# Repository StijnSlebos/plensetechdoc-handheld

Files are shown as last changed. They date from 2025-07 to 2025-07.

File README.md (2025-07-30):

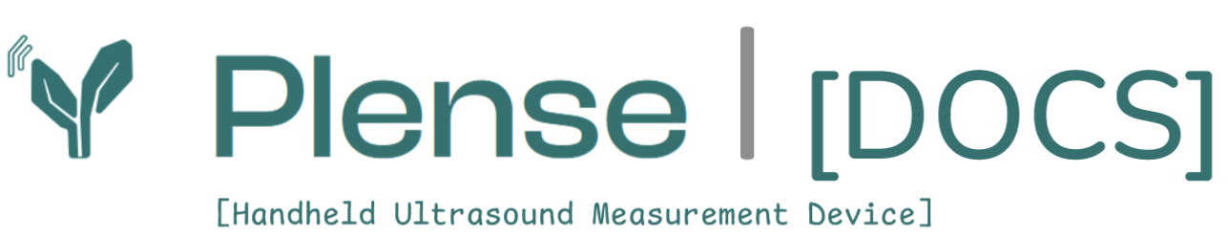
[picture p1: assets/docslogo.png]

# plensetechdoc-handheld
Documentation and code for the ultrasound handheld measuring device built by plense-technologies.

## Overview

A precision-engineered handheld setup for in-situ acoustic measurement of plant stems. The system integrates a force-controlled stepper motor clamp, dual piezoelectric transducers, and a Raspberry Pi GUI. Measurements are triggered by controlled force application and executed via a miniVNA, producing calibrated Touchstone files for further analysis.

## Features

- Arduino-based motor and endstop control
- Force sensor for precise clamping
- Dual piezo transducers for signal transmission/reception
- Signal conditioning hardware
- miniVNA for impedance/transfer measurements
- Raspberry Pi GUI for system control and data capture

---

## Repository Structure

```text
handheld-acoustic-device/
│
├── README.md                   # Top-level documentation overview
│
├── arduino-firmware/           # Firmware for stepper motor and sensor control
│   └── clamp_control.ino
│
├── raspberry-pi-gui/           # Python GUI application for Raspberry Pi
│   ├── README.md               # Installation instructions and user guide
│   ├── requirements.txt        # Python dependencies (pip)
│   ├── calibration/            # Calibration files for nanoVNA
│   │   └── calibration_10-500khz.cal
│   ├── code/                   # GUI and controller source code
│   │   └── *.py
│   └── output/                 # Output folder for measurement results
│       └── metadata.json       # JSON file storing configuration and metadata
│
└── hardware/
    ├── schematics/             # Circuit diagrams and signal conditioning chain
    │   ├── signal_conditioning_chain.pdf
    │   └── arduino_schematics.pdf
    ├── bill_of_materials.md    # Parts list (can also be .xlsx)
    ├── cad/                    # Fusion 360 design files
    │   └── ...
    └── stl/                    # 3D printable models
        └── ...

```
<p float="left">
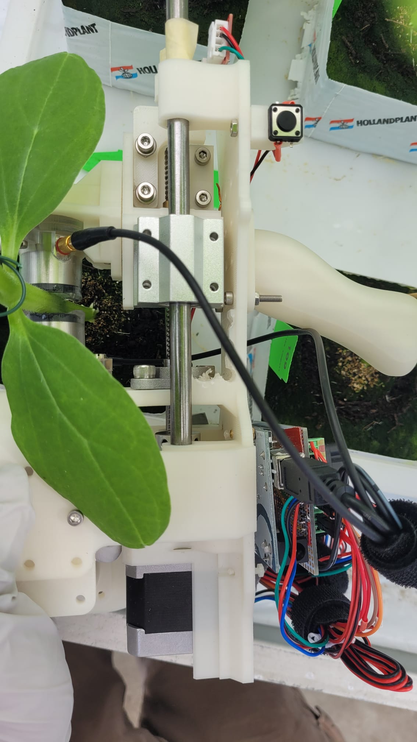
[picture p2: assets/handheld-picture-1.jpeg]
  
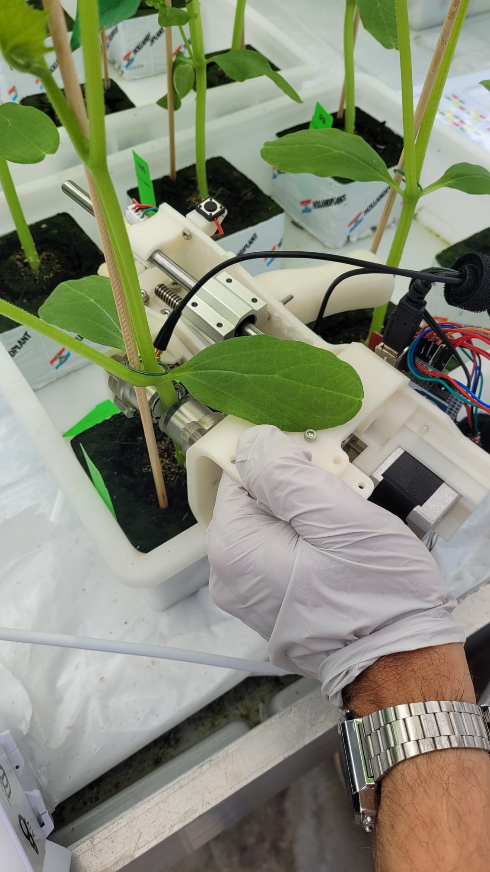
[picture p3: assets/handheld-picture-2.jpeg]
  
</p>

---

## 1. **Introduction**
Welcome to the startup guide for using our handheld plant acoustic sensing system. This document provides an overview of system components, setup procedures, operating routines, and background theory. This device and its applicability and methodology are developed by plense technologies in 2023-2025. The goal of this device is to measure accoustics through the stem of a plant and part of a sensor development project. 

The produced data from this setup can be analyzed using the [developed data-tools in this](https://github.com/StijnSlebos/plensetechdoc-dataanalysis) repository.
Our other related projects for [passive audio capture](https://github.com/StijnSlebos/plensetechdoc-passiveaudiocapture) and for the [plensor multisensor system](https://github.com/StijnSlebos/plensetechdoc-sensoredgecode) can be found in their respective repositories.

For any questions related to this project please reach into the discussiong tab (and perhaps your question is already answered there!).

Below you will walk through the system description, the setup-guide, a walkthrough of usage, a startup explanation of the data-analysis with touchstone files and lastly a troubleshooting guide. The subsections below will cover theoretical background and goals. 

### 1.1 **How It Works: Ultrasound sensing**
The system analyzes the frequency-dependent transmission characteristics of acoustic signals through the plant stem, reflecting physiological and structural traits. The stem is clamped and probed using piezo transducers, while signal analysis is conducted via the nanoVNA. Coordination is handled by the Raspberry Pi and Arduino.

### 1.2 **Theoretical Background: why would you sense ultrasound in a plant**
#### Acoustic Impedance and Frequency Transmission
- Frequency-dependent impedance and transfer response represent internal mechanical structure
- Influenced by stem stiffness, geometry, water content, and health status

#### Plant Sensing Rationale
- Transfer functions provide insights into physiological condition
- Non-destructive and consistent over time

## 2. **System Components**
_images speak louder than words_
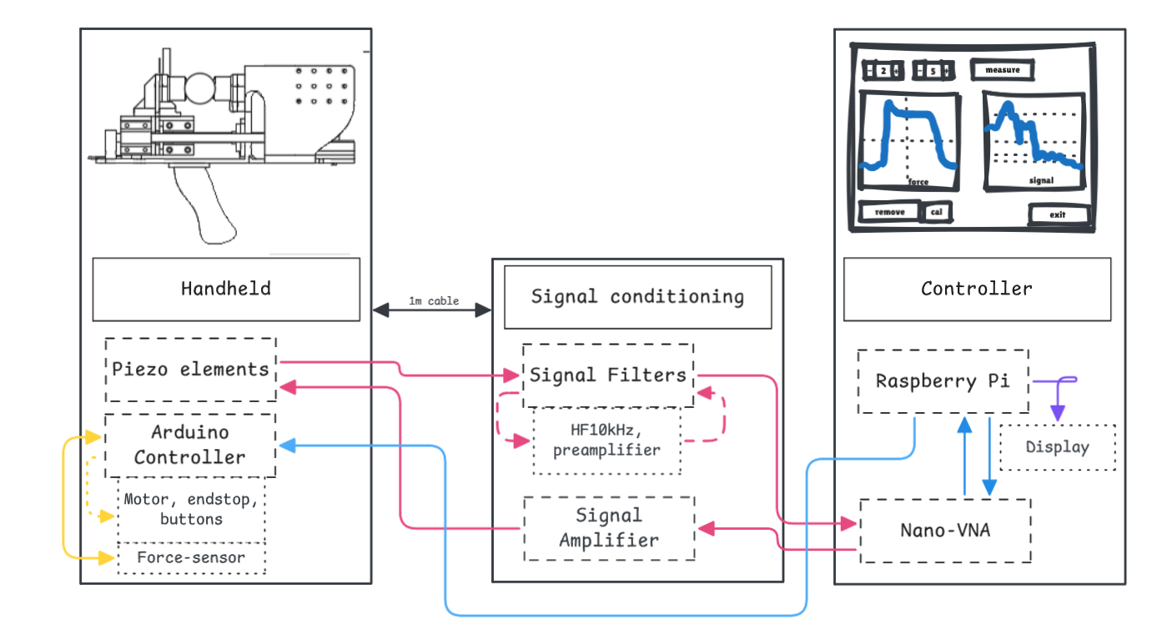
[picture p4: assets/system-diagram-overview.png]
System Overview


- Arduino-based motor and endstop control
- Force sensor for precise clamping
- Dual piezo transducers for signal transmission/reception
- Signal conditioning hardware
- nanoVNA for impedance and frequency response measurement
- Raspberry Pi GUI for system control and data capture

You might want to bring with you when going into a greenhouse for testing:
- Caliper (schuifmaat)
- Smartphone for photo documentation
- Notebook

## 3. **Setup Instructions**
If you work with an existing setup, you can skip the first segment where the construction and configuration is explained. However, it might still be good to understand the entire setup in case of troubleshooting. The arduino firmware upload is only necessary once per arduino. (an arduino is a microcontroller, it will just do whatever you configure it to on startup -> setup 🎚️ once and then loop ♻️.)

---
### Building the setup
-> see the [assembly documentation](hardware/hardware_assembly.md), BOM and cad files in this repo.
_it is all explained there!_

---
### Arduino Firmware 

> ⚠️ **Warning**: If homing does not occur immediately or endstop trigger fails, disconnect power to avoid mechanical damage.

Firmware upload is only necessary when building a new system.

For **new setups**:
- Connect the Arduino via USB to your computer or Raspberry Pi
- Use the Arduino IDE or run:  
  `arduino-cli upload -p /dev/ttyUSB0 --fqbn arduino:avr:uno clamp_control.ino`  
  (adjust port and board as needed)
- Ensure the correct board and port are selected
- After upload, if necessary reset the Arduino or power-cycle to trigger homing (generally after upload it triggers a reset; opening a serial monitor also triggers reset)

For **existing setups**:
- Ensure power is connected to both Arduino and the motor driver (black adapter)
- On power-up, the Arduino will automatically home and enter wait mode

---
### Standalone Arduino Operation (Serial Monitor)

The Arduino firmware (`clamp_control.ino`) can also operate without the GUI, using direct commands via a serial monitor.

To trigger a force-controlled clamp cycle, send the following command over the serial interface:

```bash
MOVETOFORCE <force_in_N> <hold_duration_in_s>
```

**Example**:
```bash
MOVETOFORCE 12 5
```

This moves the clamp to **12 N**, holds for **5 seconds**, then automatically returns to home position.

> ⚠️ **Force Limit**: Never exceed `15 N` to avoid damaging the clamp or sensor.

---
### Raspberry Pi GUI Setup

For the full explanation of the RaspberryPi controller/gui code, I refer to the dedicated [README.md](raspberry-pi-gui/README.md) within its folder.

Quick Startup sequence (from code-terminal or other terminal environment):
```bash
cd contact-edge-code
source venv/bin/activate
python gui.py
```

_Notes:_
- GUI may stall on message boxes — check active windows.
- The nanoVNA **does not require manual calibration**: calibration files are loaded automatically from the Raspberry Pi.
- However, the mechanical setup **must be calibrated on startup** using a 12 mm stave to align motor steps with diameter.
- Use "Single" measurement mode (~~3 repetitions does not function reliably~~).
- GUI failure mode is non-destructive; no need to delete files after crash.
      - See troubleshooting at the end of file for common errors

## 4. **Usage Workflow**
Once you have everything set up hardware wise, make sure the raspberry pi software (os and then python gui) is also ready to run. When you have the full setup ready, follow the following steps to perform a full measurement/experiment.

- Start by configuring the settings in the metadata file. This is used as settings for your experiments and makes sure all filenames and data is in proper format
- Also make sure you have some data-storage-space available. (the file sizes are not very big, but no space could cause errors)
- Once thats all set up, connect the power to the arduino (first the usb/5v to the Raspberry pi, then once that works, the 12v to the motor)
     - if homing occurs properly you can continue
- Now we can start the gui application from the raspberry pi (its above)
     - And perform the required calibration run with a 12mm stave.

Once this is all set, below the workflows for different situations.

### Clamping Routine
Once you are all set, you can:
- Position stem in clamp; this will be a bit nifty at first, but make sure everything is well in place once you press measure
- configure plant and/or node number in the GUI
- press measure or 3 reps
- hold still during the measurement
     - this will be the hard part, but this makes for better results
- Wait for automatic homing
     - the force measurement is now also finished, you can move freely again

**Per Plant Protocol:**
Some remarks on working with plants:
- Label plants if not already labeled
     - nodes might also need labeling if you measure multiple (generally greenhouses/experimental facilities have tools for this)
- Measure stem/node diameter using caliper
- Take a photo of the plant using a smartphone
- Write down specific observations (after 10 plants many things will be forgotten)

**Triggering nanoVNA**
THe nanovna is controlled through the gui, so you wont have to do anything specifically yourself:
- Use GUI to start frequency response measurement
- Ensure mechanical calibration has been completed
- If the vna does not respond properly reset or restart it

> When running in new settings, it is advised to recalibrate and update the calibration file accordingly.

**Data Retrieval**
- Measurements saved locally on Raspberry Pi
- Access via SCP or USB expor
     - _Raspberry Pi Connect_ is a nice new service worth checking out for these purposes. 

## 5. **Data Format**
The frequencyresponse (vna transfer data) files are saved in touchstone files. The force data is logged to a csv-file. The metadata(.json)file can be loaded or read to match files with measurements. 

### Metadata.json
Metadatafile in proper json format. Can be loaded in python as a dictionary containing both settings and measurement logs.

### Touchstone (.s2p)
- Standard 2-port network parameter file
- Contains frequency, magnitude, and phase of S11/S21 etc.
- Can be visualized with tools like NanoVNA Saver or MATLAB

### Force-sweep (.csv)
- Standard csv log,
- contains timestamp, microsteps (travel), distance (converted from travel) and force in newtons (N).

## 6. **Troubleshooting Guide**
### Common Problems & Tips
- Start measurements at 8:00 — helps reduce heat and avoids interference with irrigation (sproeiers)
- Time might be inaccurate if there’s no internet connection
- Use a comfortable amount of ultrasound gel — not too much, not too little
- Always calibrate using the 12 mm stave — either one is acceptable
- Calibrate hourly unless failure mode disrupts the flow, in which case recalibration might not be required
- Use keyboard and mouse due to gloves (touchscreen is unreliable)
- **Remove the dripper before starting measurements**
- Manually measured diameters are preferred — the values in `metadata.json` are unreliable

### Failure Modes
- Stop immediately if a measurement takes unusually long

### Full Restart Procedure
1. Unplug Arduino cable (on the Arduino side)
2. Exit the GUI
3. Power cycle the nanoVNA using its slider switch
4. Open Arduino IDE and check the port number:
   - Program: Arduino, under Programming
   - Tools → Port: identify the correct `/dev/ttyACM*` port
5. If needed, update the port in `motor_test.py` to match
6. Reconnect the Arduino USB cable
7. Restart the GUI and perform calibration

## 7. **Contributing & License**
- WUR and TUD Proposals
    - Proposals

- Open contributions welcome.

- Licensing details in the licence file.

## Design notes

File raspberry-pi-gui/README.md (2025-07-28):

## Force & NanoVNA Control Suite for Raspberry Pi

This repository contains scripts to:

* Control a stepper-driven indenter via Arduino for force–deflection measurements
* Perform continuous NanoVNA sweeps with automated USB power-cycling
* Manage USB hub ports for nanoVNA recovery

---

## Files

* **`gui.py`**
  **New Graphical User Interface (GUI)** for managing force-deflection and NanoVNA measurements. This fullscreen, touchscreen-friendly interface allows users to configure and initiate single or repetitive measurements, with dedicated controls for Node #, Plant #, and measurement actions (Start, Stop, Remove Previous, Restart App). It integrates the `motor_test.py` and `nanovna.py` functionalities for a streamlined workflow.

* **`arduino_force_controller.py`**
  Python class to communicate with an Arduino over serial, read force/step data, and send move commands.

* **`motor_test.py`**
  High-level measurement protocol: drives the indenter to a target force, logs force vs. deflection, and plots results. **Now includes a configurable zero_distance_mm, loaded from metadata.json, and improved resilience against Arduino communication hangs with an homing timeout.**

* **`nanovna.py`**
  Continuous NanoVNA sweep script with auto-recovery via USB power-cycling. Segments the sweep, retries on failure, and writes `.s2p` files. **Enhanced to return a success/failure boolean to the GUI, enabling robust error handling and file cleanup.**

* **`usb_controller_subprocess.py`**
  Wraps `uhubctl` calls to power-cycle a UUGear MEGA4 hub port. Used by `nanovna.py` for recovery.

* **`../arduino-firmware/clamp-control/clamp-control.ino`**
  Arduino sketch running on the Pi-connected Arduino to report force and stepper position over serial.

---

## Metadata (`output/metadata.json`)

The `output/metadata.json` file now contains enhanced logging for each measurement under the `measurement_log` array, with `us_properties` for each entry including:
*   `measurement_id`: Unique identifier for the measurement.
*   `timestamp`: ISO-formatted timestamp of the measurement.
*   `object_id` (Plant #): Identifies the specific plant being measured.
*   `node_number`: Indicates the node or sensor location.
*   `repetition`: The repetition number for the given object_id.
*   `zero_distance`: The zero reference distance used for the measurement, loaded from `input_settings`.

Other fields in `us_properties` are set to "none" by default.

---

## Prerequisites

1. **Raspberry Pi OS** (Buster or later)

2. **Enable serial port**

   ```bash
   sudo raspi-config
   # Interface Options → Serial Port → Disable shell, enable serial hardware
   ```

3. **Install system packages**

   ```bash
   sudo apt-get update
   sudo apt-get install -y python3-pip python3-venv uhubctl
   ```

---

## Python Environment Setup

### Initializing Virtual Environment

1. **Navigate to the raspberry-pi-gui directory:**

   ```bash
   cd raspberry-pi-gui
   ```

2. **Create a virtual environment:**

   ```bash
   python3 -m venv venv
   ```

3. **Activate the virtual environment:**

   ```bash
   source venv/bin/activate
   ```

   **Note**: You should see `(venv)` at the beginning of your command prompt when the virtual environment is active.

4. **Upgrade pip and install dependencies:**

   ```bash
   pip install --upgrade pip
   pip install -r requirements.txt
   ```

### Managing the Virtual Environment

- **To activate the virtual environment in future sessions (on raspberry pi):**
  ```bash
   cd raspberry-pi-gui
   source venv/bin/activate
   ```

- **To deactivate the virtual environment:**
  ```bash
   deactivate
   ```

- **To remove and recreate the virtual environment (if needed):**
  ```bash
   deactivate
   rm -rf venv
   python3 -m venv venv
   source venv/bin/activate
   pip install --upgrade pip
   pip install -r requirements.txt
   ```

**Important**: Always activate the virtual environment before running any Python scripts in this project.

---

## requirements.txt

```text
pyserial
numpy
scipy
matplotlib
pynanovna
```

---

## Arduino CLI Setup

1. **Install Arduino CLI**

   ```bash
   curl -fsSL https://raw.githubusercontent.com/arduino/arduino-cli/master/install.sh | sh
   sudo mv bin/arduino-cli /usr/local/bin/
   ```

2. **Initialize & install AVR core**

   ```bash
   arduino-cli config init
   arduino-cli core update-index
   arduino-cli core install arduino:avr
   ```

3. **Compile & upload sketch**

   ```bash
   # Navigate to the arduino-firmware directory
   cd ../arduino-firmware/clamp-control
   
   # Compile the sketch
   arduino-cli compile --fqbn arduino:avr:uno clamp-control.ino
   
   # Upload to Arduino (adjust port if needed)
   arduino-cli upload -p /dev/ttyACM0 --fqbn arduino:avr:uno clamp-control.ino
   ```

---

## Usage

1. **Run the GUI application**

   ```bash
   python gui.py
   ```

2. **Run force measurement** (legacy, primarily used by GUI)

   ```bash
   python motor_test.py
   ```

3. **Run NanoVNA sweeps** (legacy, primarily used by GUI)

   ```bash
   python nanovna.py
   ```

4. **Power-cycle USB ports manually** (if needed)

   ```bash
   python usb_controller_subprocess.py
   ```

---

## Testing on Raspberry Pi

Before running the full GUI application, it's recommended to test individual components to ensure proper hardware connectivity:

### 1. **Test Arduino Connection**
Ensure your Arduino is connected and appears as `/dev/ttyACM0` (or adjust the port in `motor_test.py`):

```bash
# Test Arduino communication
python code/motor_test.py
```

**Expected behavior**: The script should connect to Arduino, perform a force measurement, and create output files.

### 2. **Test NanoVNA Connection**
Verify NanoVNA is connected to the correct USB hub port:

```bash
# Test NanoVNA sweeps
python code/nanovna.py
```

**Expected behavior**: The script should connect to NanoVNA, perform sweeps, and save `.s2p` files.

### 3. **Test USB Hub Control**
Verify USB hub power cycling works:

```bash
# Test USB port power cycling
python code/usb_controller_subprocess.py
```

**Expected behavior**: The specified USB port should power off for 5 seconds, then power back on.

### 4. **Run Full GUI Application**
Once individual components are working:

```bash
# Run the main GUI application
python code/gui.py
```

**Expected behavior**: Fullscreen GUI should appear with measurement controls and real-time plotting.

### Troubleshooting

- **Arduino Connection Issues**: Check if Arduino appears as `/dev/ttyACM0` or `/dev/ttyACM1`
- **NanoVNA Issues**: Verify USB hub location and port numbers in `nanovna.py`
- **Permission Issues**: Ensure `uhubctl` is installed and user has sudo privileges
- **Port Conflicts**: Use `_cleanup_serial_connections()` in GUI to reset stale connections

---

## Notes

* All outputs (CSV, `.s2p`, plots) are saved in the `output/` directory.
* Adjust port names (e.g. `/dev/ttyUSB0`) and parameters at the top of each script.
* Ensure your Arduino is running `arduino.ino` and appears as `/dev/ttyACM0` (or similar).

## Architecture & Integration

This suite is composed of multiple components that work together to perform precise measurements and control actions:

- The Arduino microcontroller code (located in the `arduino-firmware/clamp-control/` folder) handles low-level control of the stepper motor and sensors. The `clamp-control.ino` sketch provides the firmware for the Arduino.
- The `arduino_force_controller.py` script serves as the interface between the Python application and the Arduino, wrapping the communication logic.
- The `motor_test.py` script uses the Arduino controller to drive the stepper motor, execute force measurements, and log results.
- The `nanovna.py` script manages continuous NanoVNA sweeps and implements auto-recovery via USB power-cycling by calling `usb_controller_subprocess.py`.
- The `usb_controller_subprocess.py` leverages the `uhubctl` tool to manage USB port power, ensuring robust device recovery in case of sweep failures.
- Each component is modular, allowing for separate testing and maintenance while collectively contributing to the measurement and control suite.

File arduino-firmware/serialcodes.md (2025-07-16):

### 📡 Serial Log Reference

This module communicates over serial at **115200 baud**. Logs, data, and error messages follow a compact and parsable format.

- All logs begin with `L#`, errors with `E#`, and data lines with `F... S...`.
- Endstop and Killstop states are printed as: `L#E:1`, `L#K:0` (1 = active, 0 = inactive).
- Force-position data follows the format: `F<force> S<step>`, e.g., `F1.234 S100`.

You can use [Arduino Serial Monitor](https://docs.arduino.cc/software/ide-v2/tutorials/ide-v2-serial-monitor) or [Python `pyserial`](https://pyserial.readthedocs.io/en/latest/pyserial.html) for reading and parsing these messages in real-time.

| Code     | Type   | Description                          | Trigger Location                  |
|----------|--------|--------------------------------------|-----------------------------------|
| L#INI    | Log    | Initialization started               | `setup()`                         |
| L#STU    | Log    | Setup complete                       | End of `setup()`                  |
| L#SST    | Log    | Start of force control command       | `parseCommand()` on success       |
| L#SER    | Log    | Serial command parse error           | `parseCommand()` on failure       |
| L#RST    | Log    | FX29 sensor reset initiated          | `resetFX29()`                     |
| L#E:[b]  | Log    | ENDSTOP status: 1 = reached, 0 = not | `setup()`                         |
| L#K:[b]  | Log    | KILLSTOP status: 1 = triggered, 0 = not | `setup()`                      |
| E#FER    | Error  | Force sensor read failure            | `readForce()` after retries fail  |
| E#STP    | Error  | Safety stop triggered                | `moveToPosition()`                |
| F[val] S[pos] | Data   | Force and step position log        | `serialForcePositionLog()`        |

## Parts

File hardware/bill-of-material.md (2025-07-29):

# BOM / Product Breakdown

| #   | Qty  | Item                                                                 |
|-----|------|----------------------------------------------------------------------|
| 1   |      | **Handheld**                                                         |
| 1.1 |      | **Mechanical Hardware**                                              |
| 1.1.1 |    | 3D Printed Frame                                                     |
| 1.1.1.1 | 1 each | FDM printed parts                                              |
|     | 1    | fixed-piezo-frame_frame.stl                                          |
|     | 1    | fixed-piezo-frame_frame_handheld-a.stl                               |
|     | 1    | fixed-piezo-frame_frame_handheld-b.stl                               |
|     | 1    | fixed-piezo-frame_frame_standelement.stl                             |
|     | 1    | moving-piezo-frame_frame_a.stl                                       |
|     | 1    | moving-piezo-frame_frame_b.stl                                       |
|     | 1    | endstop_v3.stl                                                       |
| 1.1.1.2 |   | Resin Printed in Elastic 50A                                        |
|     | 1    | pzo_forcesensor_hull.stl                                             |
|     | 2    | pzo_hull.stl                                                         |
|     | 1    | pzo_vibrationbase.stl                                                |
| 1.1.1.3 |   | Inserts and Screws                                                  |
|     | 25   | M3 threaded insert                                                   |
|     | 27   | M3 bolt (various lengths)                                            |
|     | 2    | M5 threaded insert                                                   |
|     | 2    | M5 bolt                                                              |
| 1.1.2 |     | Mechanical Slider Parts                                             |
|     | 2    | 200mm × 8mm linear rail                                              |
|     | 1    | 140mm × 8mm spindle/leadscrew                                        |
|     | 1    | TR8x8 leadscrew nut                                                  |
|     | 2    | SC8UU linear bearing                                                 |
|     | 1    | KFL8 bearing                                                         |
|     | 1    | 8mm flexible motor coupler                                           |
| 1.2 |      | **Electronic Hardware**                                              |
| 1.2.1 |    | Sensor and Actuator Hardware                                         |
|     | 1    | Nema17 stepper motor                                                 |
|     | 1    | Mechanical endstop                                                   |
|     | 1    | FX29 force sensor (I2C, 50N range)                                   |
|     | 1    | (Optional) pushbutton                                                |
| 1.2.2 |    | (Micro)Controller Hardware                                           |
|     | 1    | Arduino Uno (Rev 3+)                                                 |
|     | 1    | Arduino Uno protoshield (custom connections)                         |
|     | 1    | DRV8825 stepper driver                                               |
|     | -    | Wires, connectors, etc.                                              |
| 1.3 |      | **Acoustic Hardware**                                                |
|     | 2    | VS45-H Piezo element (vallen.de)                                     |
|     | 2    | Shielded cable: microdot - BNC                                       |
| 2   |      | **Signal Conditioning**                                              |
| 2.1 |      | Signal Conditioning                                                  |
|     | 1    | AEP5H preamplifier (vallen.de)                                       |
|     | 1    | DCPL2 decoupling unit (vallen.de)                                    |
|     | 1    | EF121 HF filter (Thorlabs)                                           |
|     | 1    | DLPCA-200 amplifier (femto) (+ power supply)                         |
|     | 4    | Shielded cable: BNC                                                  |
| 3   |      | **Controller**                                                       |
| 3.1 |      | Controller                                                           |
|     | 1    | Raspberry Pi 4B                                                      |
|     | 1    | VNA: Nanovna-H4                                                      |
| 3.2 |      | Miscellaneous                                                        |
|     | -    | RPI-touchscreen (or other screen)                                    |
|     | -    | RPI-mouse and keyboard (or other M&K set)                            |
|     | -    | USB cables (VNA–RPI, Arduino–RPI)                                    |
|     | -    | Power supplies                                                       |

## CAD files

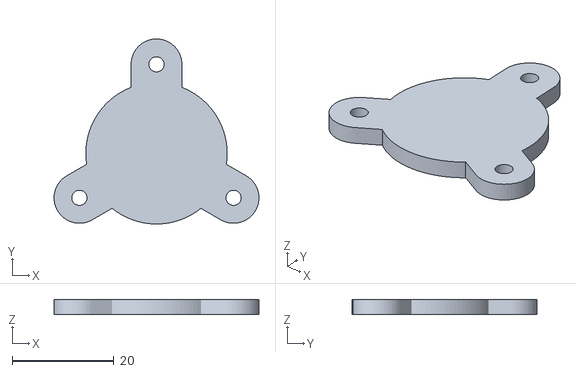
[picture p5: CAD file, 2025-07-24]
hardware/stl/pzo_vibrationbase.stl
40.3 x 36.4 x 3.00

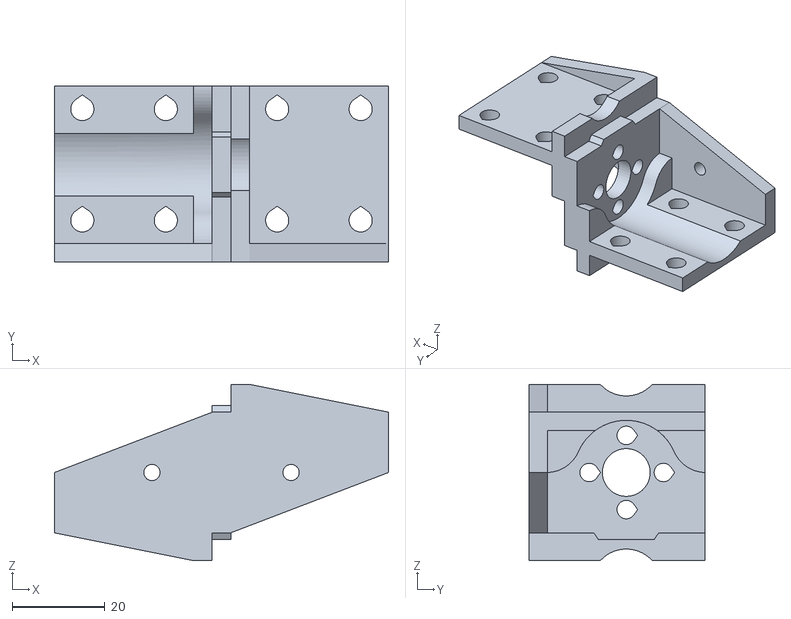
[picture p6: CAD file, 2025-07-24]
hardware/stl/moving-piezo-frame_frame_a.stl
72.0 x 38.0 x 38.0

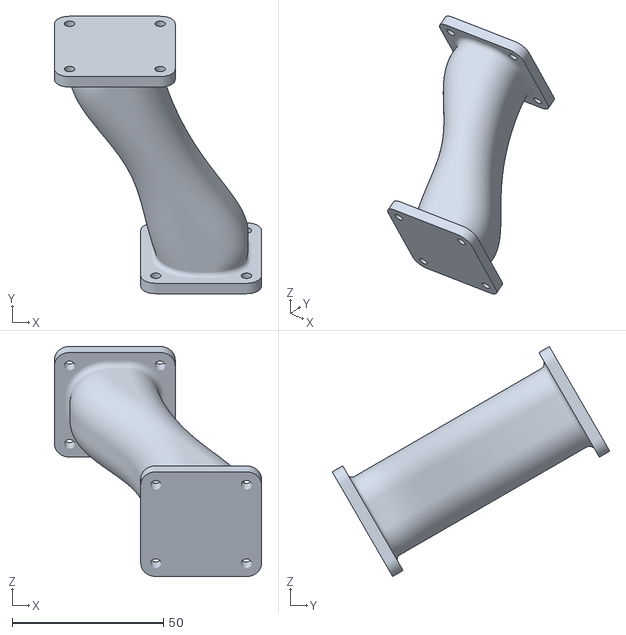
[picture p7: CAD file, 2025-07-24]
hardware/stl/fixed-piezo-frame_frame_handheld-b.stl
68.6 x 91.9 x 76.1

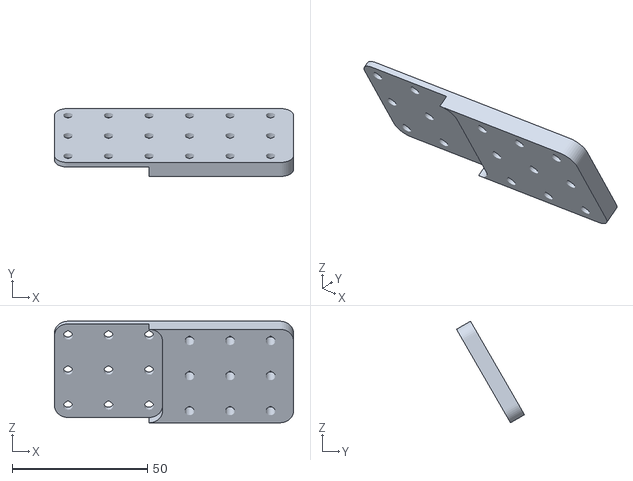
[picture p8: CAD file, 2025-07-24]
hardware/stl/fixed-piezo-frame_frame_standelement.stl
88.5 x 25.2 x 37.6

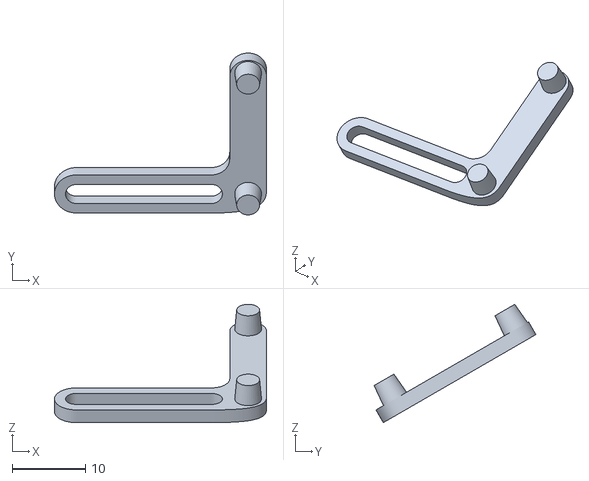
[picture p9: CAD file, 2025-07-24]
hardware/stl/endstop_v1.stl
28.9 x 22.0 x 16.1

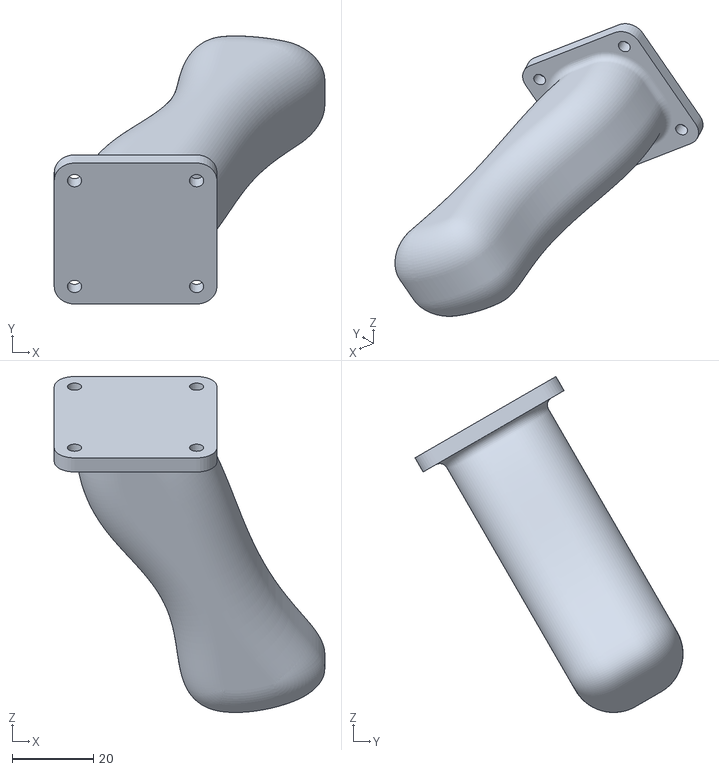
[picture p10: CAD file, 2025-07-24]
hardware/stl/fixed-piezo-frame_frame_handheld-a.stl
66.5 x 65.9 x 82.6

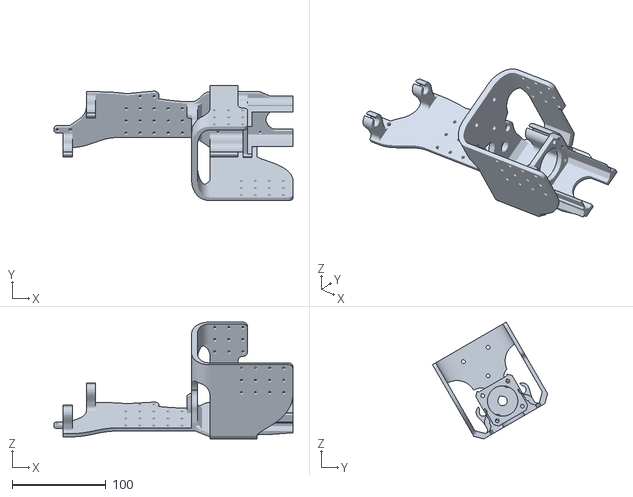
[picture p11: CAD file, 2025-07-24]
hardware/stl/fixed-piezo-frame_frame.stl
255.1 x 122.9 x 124.7

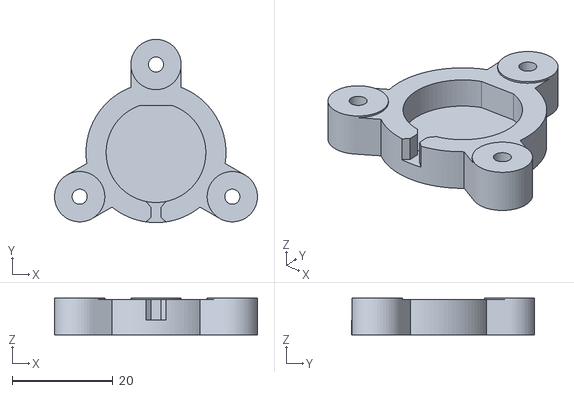
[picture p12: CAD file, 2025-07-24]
hardware/stl/pzo_forcesensor_hull.stl
40.3 x 36.4 x 7.30

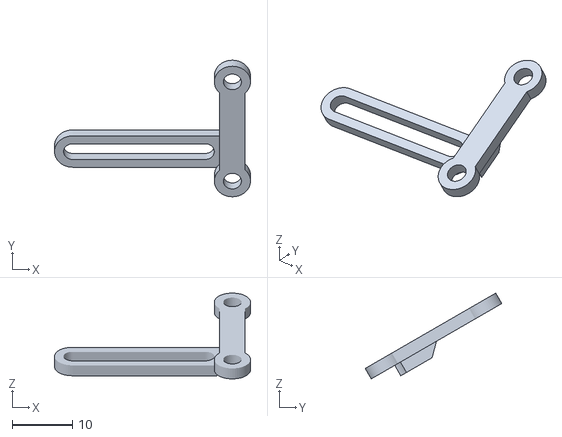
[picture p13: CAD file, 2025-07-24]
hardware/stl/endstop_v3.stl
32.5 x 22.7 x 14.2

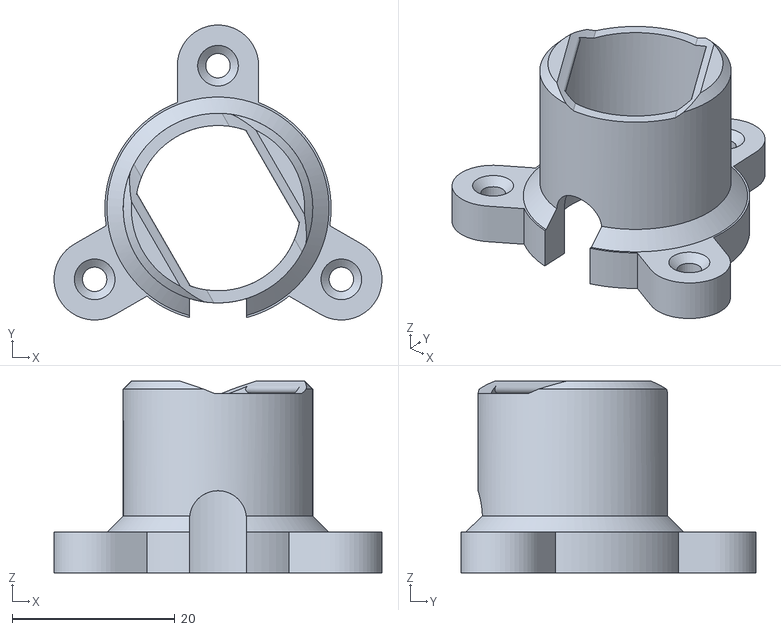
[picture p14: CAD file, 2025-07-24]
hardware/stl/pzo_hull.stl
40.3 x 36.2 x 23.6

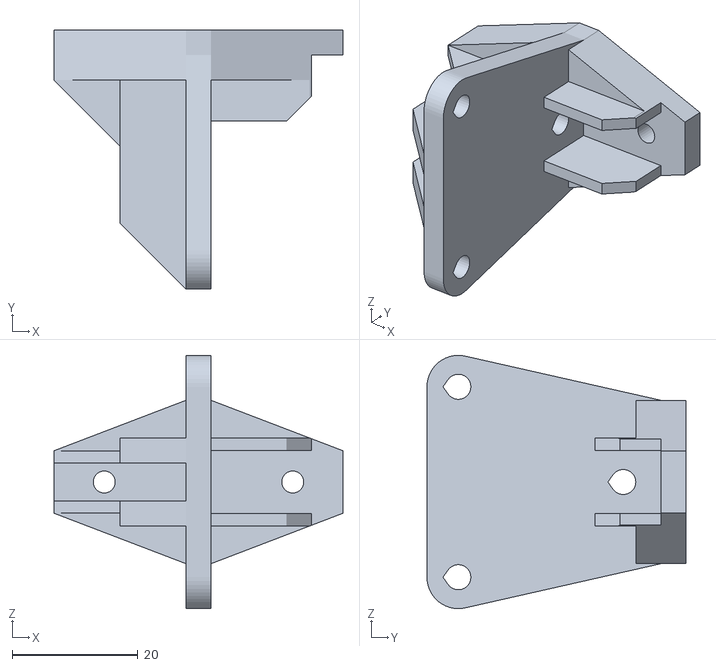
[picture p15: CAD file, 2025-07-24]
hardware/stl/moving-piezo-frame_frame_b.stl
46.0 x 41.2 x 40.3

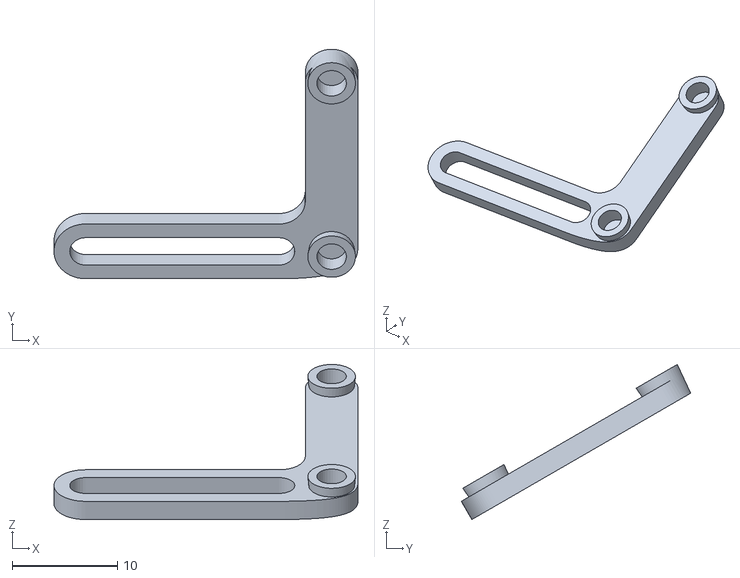
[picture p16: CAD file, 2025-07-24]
hardware/stl/endstop_v2.stl
28.9 x 21.8 x 14.7

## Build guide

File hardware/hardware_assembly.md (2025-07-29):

## **Hardware Assembly**
TO build the entire handheld device with controller make sure you have to following at hand:
- 3D printer (FDM)
- 3D Resin printer (not strictly necessary, for accoustic decoupling of piezo elements)
- Solder station + materials like wires, solder, connectors, etc.
- PC & Internet Connection: to flash your RPI sd-card and pull the code
- Preferably a way to interact with the fusion (.f3x) assembly file (can be done online)
- All Components on the [Bill-of-materials](bill-of-material.md)

---
### **3D printed parts**
Preferably print all the parts in the FMD tab of the BOM with a strong material like abs/asa on high infill (100%). THis is not required, per strict, PLA and lower infills down to 15% should also work.

For the resin printed parts, in our assembly we have constructed them from Elastic50A resin with a formlabs 3 printer. An elastic TPU might also work with FDM. The printed parts are quite small, it might be worth looking online to order at an on demand printfarm if you do not have access to a (resin) printer

---
### **Assembly of handheld**

For assembling the handheld, the easiest way would be to open the assembly from the fusion file. This way, the goal configuration is known to you. Since it is quite a puzzle to get everything aligned, it is best to keep everything loose for as long as possible. However, you will probably not solve the puzzle in one go and will have to deconstruct some parts to fit everything together. (just saying :) )

Once you have an idea of construction, start with inserting the threaded inserts in their designated spots. (not all holes need them, only if you like, you also add them on the holes on the grid where you will place the handholds. These can also be fixed with nuts.)

Now its probably easiest to construct roughly in this order:
- Start with the sliding frame (2 3d-printed parts, a leadscrew nut and 2 linear bearings)
- now fix (loosely) the bearing on the frame
- _(maybe a good time to add the piezos now, it is harder but not impossible later)_
- _(if you do so, dont forget the force-sensor)_
- add the leadscrew to your sliding frame
- put sliding frame in the fixed frame and slide in the 2 sldiing axes
- now couple the motorcouple to the motor and insert together in your assembly
-  _(later and harder moment to add piezos, might be the more safe moment since they are very expensive)_
- add the endstopslider and endstop on desired distance from your slider
- fix the arduino somewhere to your liking, a case might be a nice addition in the future
- cables, cables, cables
- **At least check if your endstop is working before powering up**

---
### **Electronics**
Soldering, electronics, that stuff. I uploaded a schematic [here](schematics/electronics-schematic.png). Its below as well:
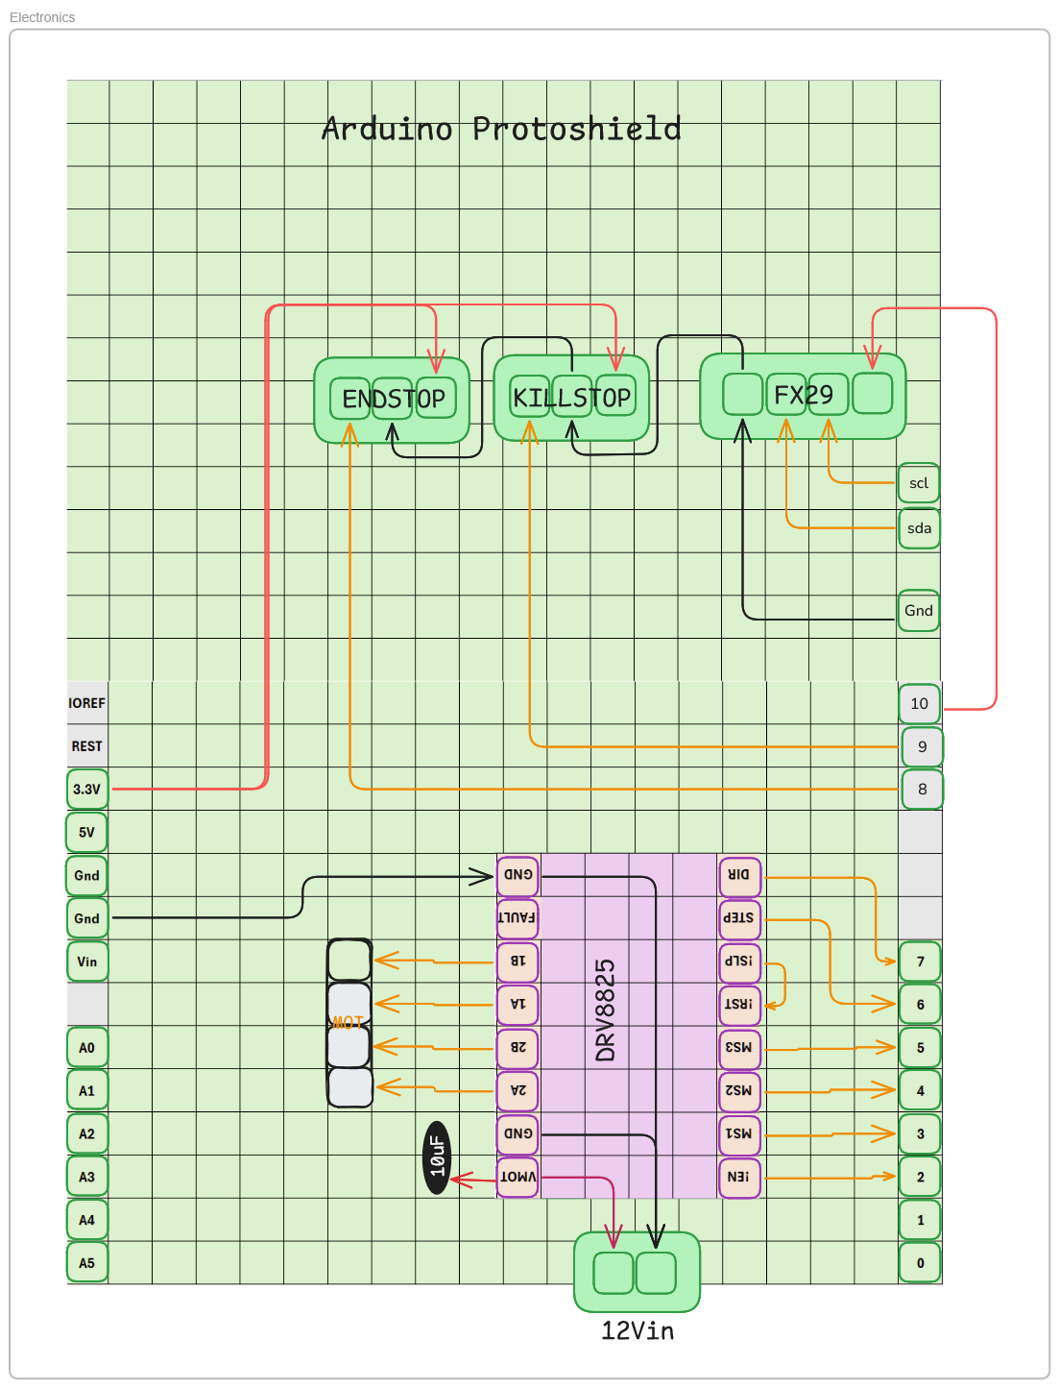
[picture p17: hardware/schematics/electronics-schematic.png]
full image thing
.

- The green things are connectors, in my case screwterminals.
- I added some header pins so I could replace the DRV8825 in case of a fire (these things seem to be quite volatile when overloaded).
- Theres a capacitor to stabilize the 12v power
- I also added a little fan on top, just connected it to the 12v as well.
- Arduinos have a weird shifted layout, the specific protoboard helps with that, otherwise it will become a bigger puzzle. (or just get a board with a logical layout :) )

- For the NEMA motor and driver, you will need to tune the current level and make sure the connectors are right.
- best is to look at this [arduino forum](https://forum.arduino.cc/t/update-current-adjustment-for-motor-drivers-drv8825-a4988/400151) for tuning current limits.
- For the motor orientation, a stepper has 2 coils, you can check with a multimeter which pins correspond to which coil. Normally it is 4 pins in a row: coil1pin1,coil1pin2,coil2pin1,coil2pin2. Meaning, if you switch your connector around, your motor will move to other direction!
- this is probably the right place for some warnings

> ⚠️ **Warning:** Always double-check motor wiring before powering the system. Incorrect connections can cause permanent damage to the driver, motor, or power supply.

> ⚠️ **Warning:** Set the motor driver's current limit before operation. Running without proper current limiting can overheat and permanently damage the motor or driver.

---
### **Signal chain**
Now for the signal chain, it might be worth to invest some time in understanding and potentially improving your conditioning hardware. We worked with what we had available in the office but think there is probably some more optimal composition if time is put in. If you work with what we have, go to the [signal-chain](schematics/signal-loop.png) and copy!
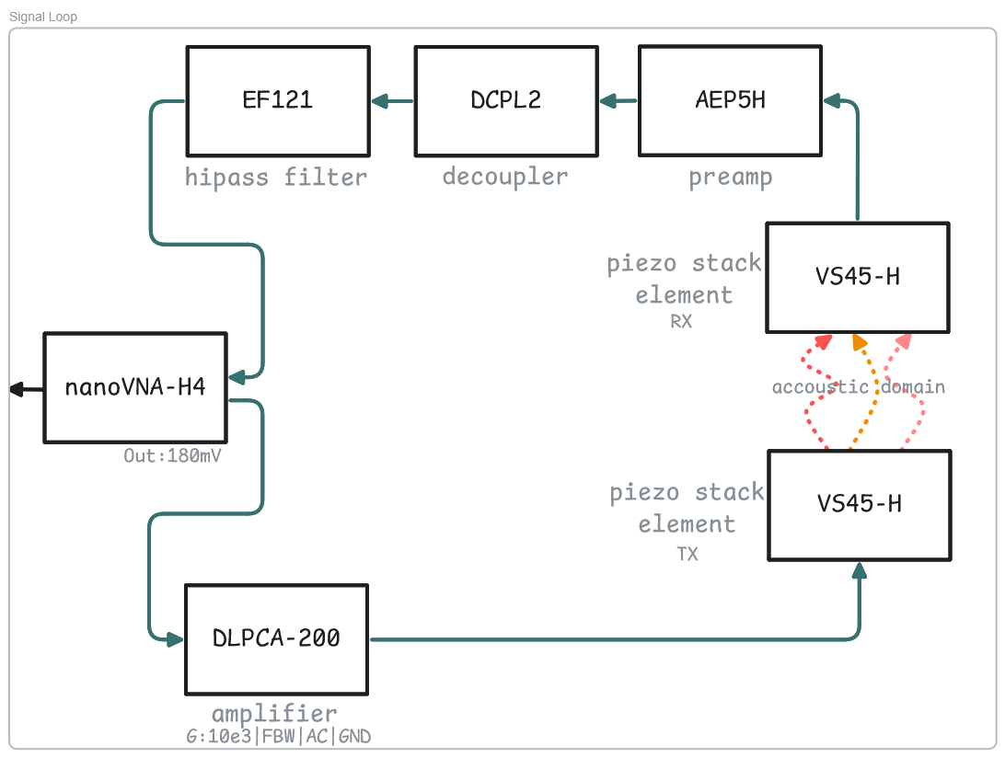
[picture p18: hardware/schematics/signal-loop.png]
signals yay!


> !please! , if you work with this specific setup, mind the settings of the amplifier, they are in the schematic!

---
### **Raspberry Pi?**
Most things considered, the raspberry pi specifics are explained here: [specific rpi readme!](../raspberry-pi-gui/README.md).
Even though, if you have not worked with it before, here are the things you need to know to get started:

- A raspberry pi is just a tiny computer running of a distribution of linux. and with a lot of I/O capabilities.
- It runs of an sd card, which you will need to flash before it works (meaning shoving the operating system (OS) on the card).
- In this case it runs python and some packages to communicate with the VNA and with the Arduino, controlling the full thing.
- The VNA and Arduino are connected over USB.
- Generally a mouse and keyboard helps
- The GUI (graphical user interface) needs a screen to work.

---

I think you should be good to go now, if you have doubts or questions, please check out the [discussions](https://github.com/StijnSlebos/plensetechdoc-handheld/discussions) page!

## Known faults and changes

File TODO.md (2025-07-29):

- README chapter 4
- README chapter 5
- README chapter 7

then we are done!

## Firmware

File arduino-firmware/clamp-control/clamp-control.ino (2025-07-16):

// Fx29 Force Control Module
// Copyright (c) 2025 Stijn Slebos, Thijs Bieling, Plense Technologies
// Licensed under the MIT License.
// This software includes code originally developed by Plense Technologies.
// If used or modified in derived works, this notice must remain in the file header,
// unless explicit permission is granted by the repository owner to remove or alter it.

// Arduino sketch to control a stepper-actuated force application using the FX29 load cell.
// Commands via serial (MOVETOFORCE) allow precise positioning based on a force target.
// Endstop logic ensures mechanical safety. Motor speed adapts based on force error.

#define STEP_PIN 6
#define DIR_PIN 7
#define MS1_PIN 3
#define MS2_PIN 4
#define MS3_PIN 5
#define KILLSTOP 8
#define ENDSTOP 9
#define ENABLE_PIN 2
#define FX29_POWER_PIN 10

#define CONVERSION_DELAY_MS 3

#include <Wire.h>
#define FX29_ADDR 0x28
#define MAXFORCE 15

#define MOTORSLOW 50
#define MOTORMID 200
#define MOTORFAST 500

#include <AccelStepper.h>
AccelStepper stepper(AccelStepper::DRIVER, STEP_PIN, DIR_PIN);

String inputBuffer = "";

bool executeflag = false;
bool errorflag = false;

float forceSetpoint = 5;
int timedelaySeconds = 1;

// Resets the FX29 sensor by cycling power
int resetFX29() {
  Serial.println("L#RST");
  digitalWrite(FX29_POWER_PIN, LOW);
  delay(100);
  digitalWrite(FX29_POWER_PIN, HIGH);
  delay(100);
  Wire.beginTransmission(FX29_ADDR);
  if (Wire.endTransmission() != 0) return -2;
  delay(CONVERSION_DELAY_MS);
  return 1;
}

// Reads raw force sensor value from FX29
int readForceFromSensor() {
  Wire.requestFrom(FX29_ADDR, 2);
  delay(CONVERSION_DELAY_MS);
  unsigned long startTime = millis();
  while (Wire.available() < 2) {
    if (millis() - startTime > 10) return -3;
  }
  uint8_t msb = Wire.read();
  uint8_t lsb = Wire.read();
  return ((msb & 0x3F) << 8) | lsb;
}

// Converts raw FX29 value to Newtons
float convertToNewton(int raw) {
  return 0.00308 * (raw - 850);
}

// Performs robust force read with retries and sensor resets
float readForce() {
  const int maxRetries = 5;
  const int maxResetIterations = 2;
  for (int iteration = 0; iteration <= maxResetIterations; iteration++){
    for (int attempt = 0; attempt <= maxRetries; attempt++) {
      int raw = readForceFromSensor();
      if (raw > 0 && raw < 16383) return convertToNewton(raw);
    }
    resetFX29();
  }
  Serial.println("E#FER");
  errorflag = true;
  return -1;
}

// Returns true if digital input pin is pulled LOW
bool endstopReached(int pin){
  return (digitalRead(pin) == LOW);
}

// Outputs force and position log over serial
void serialForcePositionLog(float currentForce, int currentPosition){
  Serial.print("F"); Serial.print(currentForce, 3); Serial.print(" S"); Serial.println(currentPosition);
}

// Configures motor driver for full-step mode
void setMicrostepping() {
  digitalWrite(MS1_PIN, LOW);
  digitalWrite(MS2_PIN, LOW);
  digitalWrite(MS3_PIN, LOW);
}

// Calculates error between target and current force
float getForceError(float targetForce, float currentForce) {
  return targetForce - currentForce;
}

void enableMotor(){ digitalWrite(ENABLE_PIN, LOW); }
void disableMotor(){ digitalWrite(ENABLE_PIN, HIGH); }

// Adjusts motor speed based on force error magnitude
void updateCurrentSpeedOnError(float forceError){
  if (abs(forceError) > 3.0) stepper.setSpeed(-1*MOTORMID);
  else stepper.setSpeed(-1*MOTORSLOW);
}

// Main loop to move actuator until target force is reached or a stop condition is hit
void moveToPosition(float targetForce) {
  enableMotor();
  errorflag = false;
  float currentForce = readForce();
  unsigned long previousTime = 0;
  const unsigned long interval = 10;
  float forceError = 10;

  while (abs(forceError) > 0.5 && forceError > -1 && timedelaySeconds >= 0) {
    if (endstopReached(ENDSTOP) || endstopReached(KILLSTOP) || currentForce > MAXFORCE || errorflag) {
      timedelaySeconds = -1;
    }
    unsigned long currentTime = millis();
    if (currentTime - previousTime >= interval) {
      previousTime = currentTime;
      currentForce = readForce();
      int currentPosition = stepper.currentPosition();
      forceError = getForceError(targetForce, currentForce);
      updateCurrentSpeedOnError(forceError);
      serialForcePositionLog(currentForce, currentPosition);
    }
    stepper.runSpeed();
  }

  if (timedelaySeconds < 0) {
    Serial.println("E#STP");
    delay(1000);
  }
  disableMotor();
}

// Maintains position and logs force for a given delay
void waitOnPosition(int timedelayms) {
  unsigned long start = millis();
  float currentForce = 0;
  while (millis() - start < timedelayms) {
    if (! errorflag) currentForce = readForce();
    int currentPosition = stepper.currentPosition();
    serialForcePositionLog(currentForce, currentPosition);
    delay(10);
  }
}

// Reads and parses serial input commands
String handleSerialInput() {
  while (Serial.available()) {
    char c = Serial.read();
    if (c == '\n' || c == '\r') {
      if (inputBuffer.length() > 0) {
        String result = parseCommand(inputBuffer);
        inputBuffer = "";
        return result;
      }
    } else {
      inputBuffer += c;
    }
  }
  return "";
}

// Parses and executes the MOVETOFORCE serial command
String parseCommand(String cmd) {
  cmd.trim();
  if (cmd.startsWith("MOVETOFORCE")) {
    int idx1 = cmd.indexOf(' ');
    int idx2 = cmd.indexOf(' ', idx1 + 1);
    if (idx1 > 0 && idx2 > idx1) {
      forceSetpoint = cmd.substring(idx1 + 1, idx2).toFloat();
      timedelaySeconds = cmd.substring(idx2 + 1).toInt();
      executeflag = true;
      return "L#SST";
    }
  }
  return "L#SER";
}

// Moves motor to endstop and resets position to zero
void homeSequence() {
  enableMotor();
  stepper.setSpeed(MOTORFAST);
  unsigned long previousTime = 0;
  const unsigned long interval = 10;
  float currentForce = 0;

  while (!endstopReached(ENDSTOP) && !endstopReached(KILLSTOP)) {
    unsigned long currentTime = millis();
    if (currentTime - previousTime >= interval) {
      previousTime = currentTime;
      if (! errorflag) currentForce = readForce();
      int currentPosition = stepper.currentPosition();
      serialForcePositionLog(currentForce, currentPosition);
    }
    stepper.runSpeed();
  }

  stepper.setCurrentPosition(0);
  stepper.moveTo(-200);
  while (stepper.distanceToGo() != 0) stepper.run();
  executeflag = false;
  disableMotor();
}

// System initialization
void setup() {
  stepper.setMaxSpeed(800.0);
  stepper.setAcceleration(1000.0);
  stepper.setCurrentPosition(0);

  pinMode(MS1_PIN, OUTPUT);
  pinMode(MS2_PIN, OUTPUT);
  pinMode(MS3_PIN, OUTPUT);
  pinMode(KILLSTOP, INPUT_PULLUP);
  pinMode(ENDSTOP, INPUT_PULLUP);
  pinMode(ENABLE_PIN, OUTPUT);
  pinMode(FX29_POWER_PIN, OUTPUT);

  Wire.begin();
  Serial.begin(115200);

  setMicrostepping();
  disableMotor();
  
  Serial.print("L#INI");
  resetFX29();  
  delay(100);
  
  Serial.println("L#STU");
  Serial.print("L#E:"); Serial.println(endstopReached(ENDSTOP));
  Serial.print("L#K:"); Serial.println(endstopReached(KILLSTOP));
  delay(100);
  Serial.print("L#E:"); Serial.println(endstopReached(ENDSTOP));
  Serial.print("L#K:"); Serial.println(endstopReached(KILLSTOP));

  homeSequence();
}

// Main loop that waits for serial input or executes movement
void loop() {
  if (! executeflag) {
    String result = handleSerialInput();
    if (result.length() > 0) Serial.println(result);
  }
  if (executeflag) {
    moveToPosition(forceSetpoint);
    if (timedelaySeconds > 0) waitOnPosition(timedelaySeconds * 1000);
    homeSequence();
  }
}
